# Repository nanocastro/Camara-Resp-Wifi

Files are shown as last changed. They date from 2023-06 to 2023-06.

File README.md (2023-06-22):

# Cámara de respiración de suelo

Prototipo portátil y de bajo costo para medir el flujo de CO2, la temperatura y la humedad del suelo y estimar su actividad microbiana.  

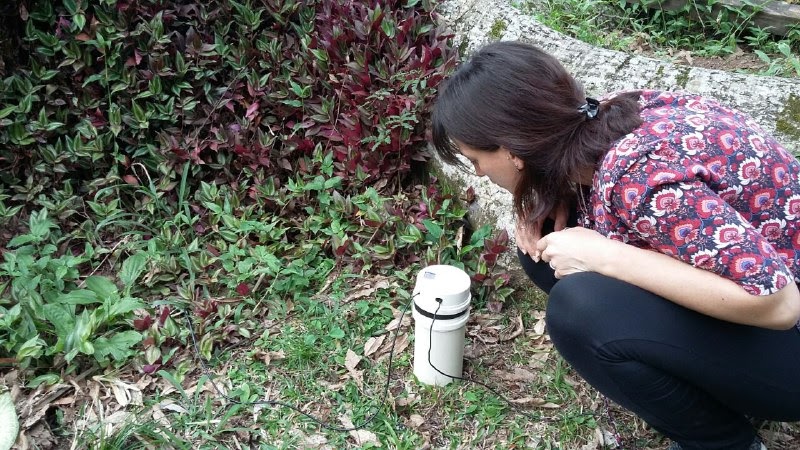
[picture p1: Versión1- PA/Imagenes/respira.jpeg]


Este prototipo es parte del trabajo que estamos desarrollando en el [Laboratorio agroecológico abierto](https://regosh.libres.cc/proyectos/lab-agroeco-abierto/) y el nodo [ReGOSH de Mendoza](https://regosh.libres.cc/).

Su desarrollo está basado en el [prototipo abierto de Hackteria](https://www.hackteria.org/wiki/CO2_Soil_Respiration_Chamber).  

El costo de este prototipo es de 2 órdenes de magnitud menor que el de una [cámara comercial](https://gitlab.com/nanocastro/camara-respiracion-suelo/-/blob/master/Presupuestos%20Nro%2012426.PDF).  

## Prototipos
Estos prototipos están aún en fase de desarrollo. Necesitamos testear en campo y mejorar la documentación y el diseño.

### Prototipo actual - Versión Mendoza

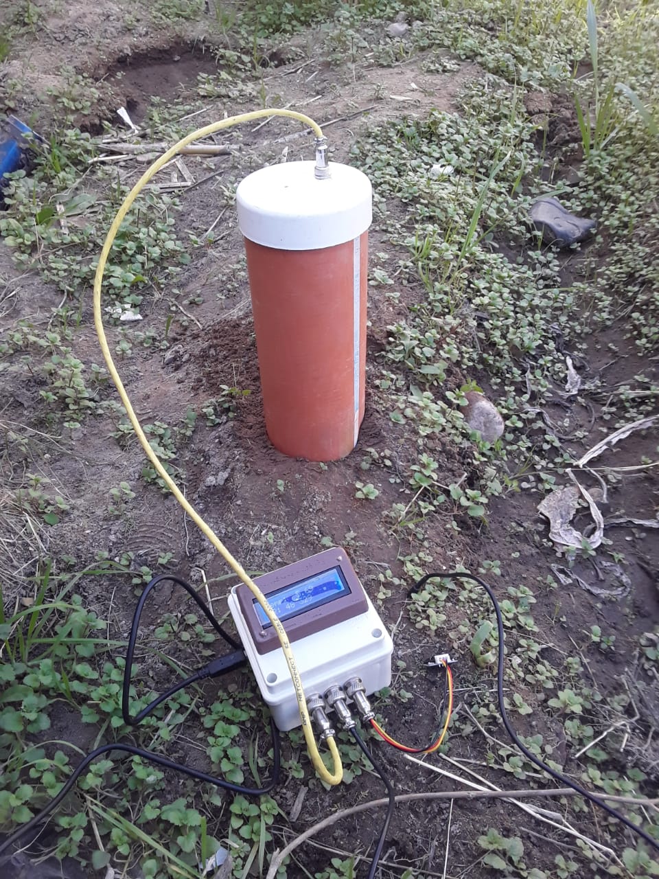
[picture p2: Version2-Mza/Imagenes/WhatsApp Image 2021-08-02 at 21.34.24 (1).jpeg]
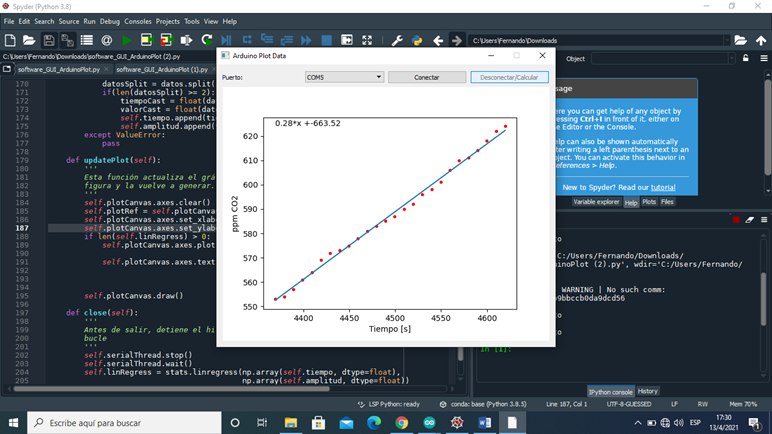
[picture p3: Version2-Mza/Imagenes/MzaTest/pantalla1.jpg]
 

Este prototipo utiliza el sensor de CO2 infrarrojo MH-Z19B que se coloca en el interior de una cámara para medir el flujo de CO2 y es controlado por una placa Arduino UNO. Los datos son transmitidos por bluetooth a un script de python que recibe los datos, los grafica en tiempo real y calcula la regresión lineal de un intervalo deseado. El dispositivo mide también la temperatura y la humedad de suelo

> [Aquí la documentación completa](/Version2-Mza) 

### Primer prototipo - Residencia Porto Alegre

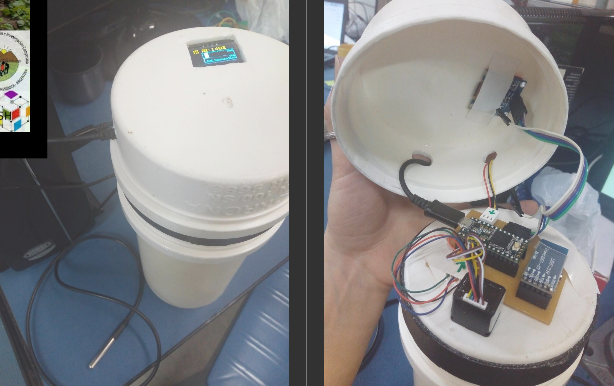
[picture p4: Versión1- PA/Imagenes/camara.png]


[Primer prototipo](/Versión1-%20PA) desarrollado en el marco de la residencia ReGOSH (Porto Alegre) financiadas por CYTED.   
Este dispositivo utiliza un sensor MH-Z16 y una placa Teensy 4.0. Los datos se visualizan en una pantalla OLED

### Cómo funciona y para que sirve una cámara de respiración de suelo?
[Aqui](/Referencias) puedes encontrar algunos documentos que explican el funcionamiento de las cámaras de respiración de suelo y presentan algunos de sus usos

### Licencia 
Este proyecto es de código abierto y se libera bajo [licencia CERN para hardware abierto](https://gitlab.com/nanocastro/camara-respiracion-suelo/-/blob/master/License). 

### Te interesa colaborar?

Si te interesa el proyecto y quisieras colaborar podes escribirnos a 

ferhcastro at gmail.com o pcremades at gmail.com

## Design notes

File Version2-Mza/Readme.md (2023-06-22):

# Cámara de Respiración de Suelo: Guía de armado
__Nodo reGOSH Mendoza - Equipo de Física Experimental II, FCEN - 2022__
## Descripción del dispositivo
El dispositivo puede medir la concentración de CO2, la temperatura y la humedad del suelo.  

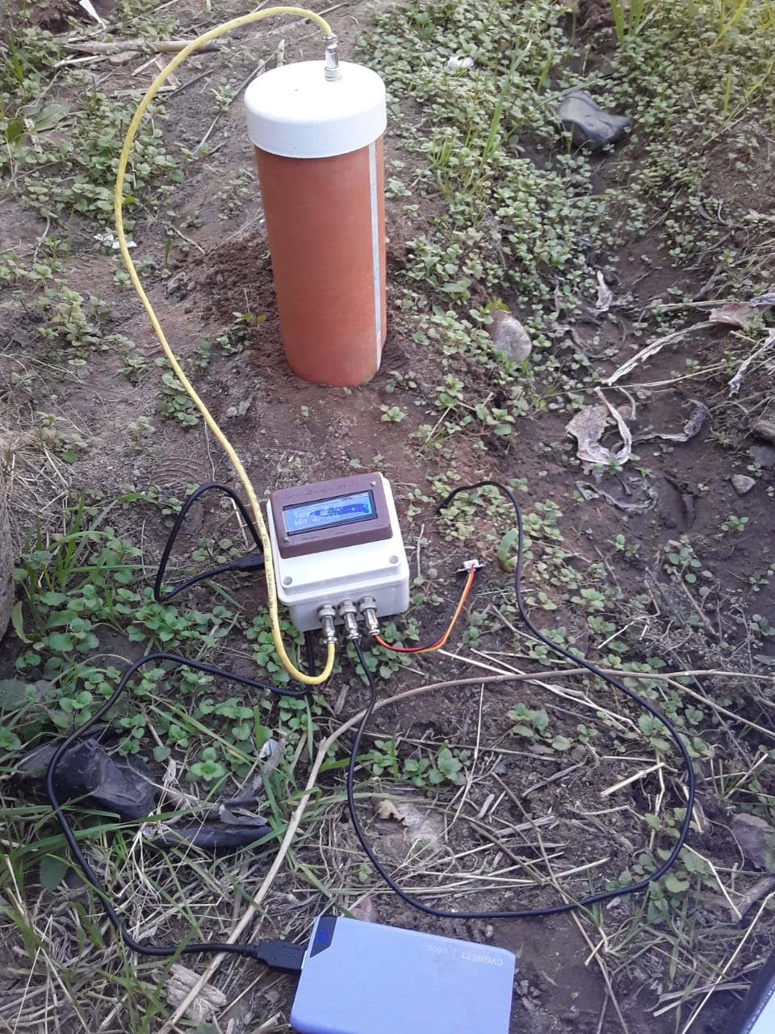
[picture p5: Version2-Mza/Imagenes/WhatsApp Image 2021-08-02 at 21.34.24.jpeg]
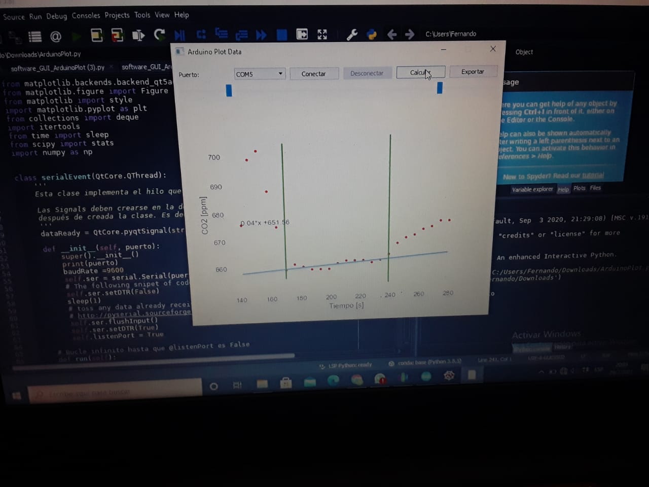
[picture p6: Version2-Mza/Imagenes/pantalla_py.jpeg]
 

## BOM
[Lista de materiales](/Version2-Mza/ListaMateriales.ods)

## Ensamblado
El dispositivo cuenta con 2 partes, una cámara donde se aloja el sensor de CO2 y una unidad de control que se encarga de la comunicación con los sensores y de enviar lsos datos vía bluetooth a una PC donde se pueden visualizar y analizar. 
__Herramientas necesarias:__

* Soldador de estaño
* Pistola de silicona
* 4 tornillos de 2 cm
* Alicate
* Taladro
* Mecha para taladro de 18mm

## (2) Cableado y test inicial
En primer lugar debemos probar que la electrónica funcione correctamente, para ello:

* Realizamos el cableado según la figura:

Atención! El módulo bluetooth lo debemos conectar luego de que esté cargado el firmware.
  
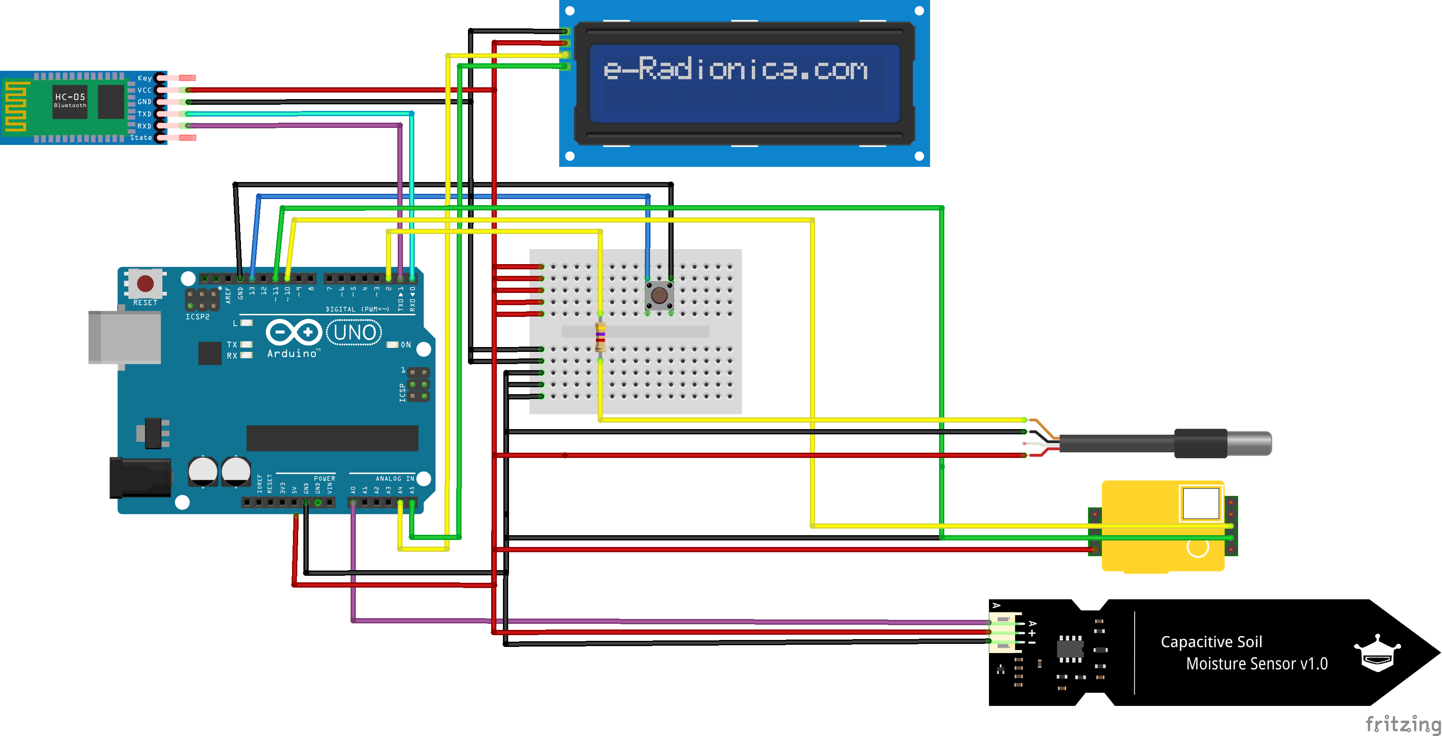
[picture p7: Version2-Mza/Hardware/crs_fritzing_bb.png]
Esquematico Fritzing
   

### Ensamblado cámara de respiración
La cámara está compuesta por un tramo de 15-20cm de caño sanitario de 110mm y una tapa para dicho caño.   
  
Una vez que hemos comprobado el correcto funcionamiento del dispositivo podemos colocar y cablear el sensor de CO2 dentro de la cámara de respiración.  

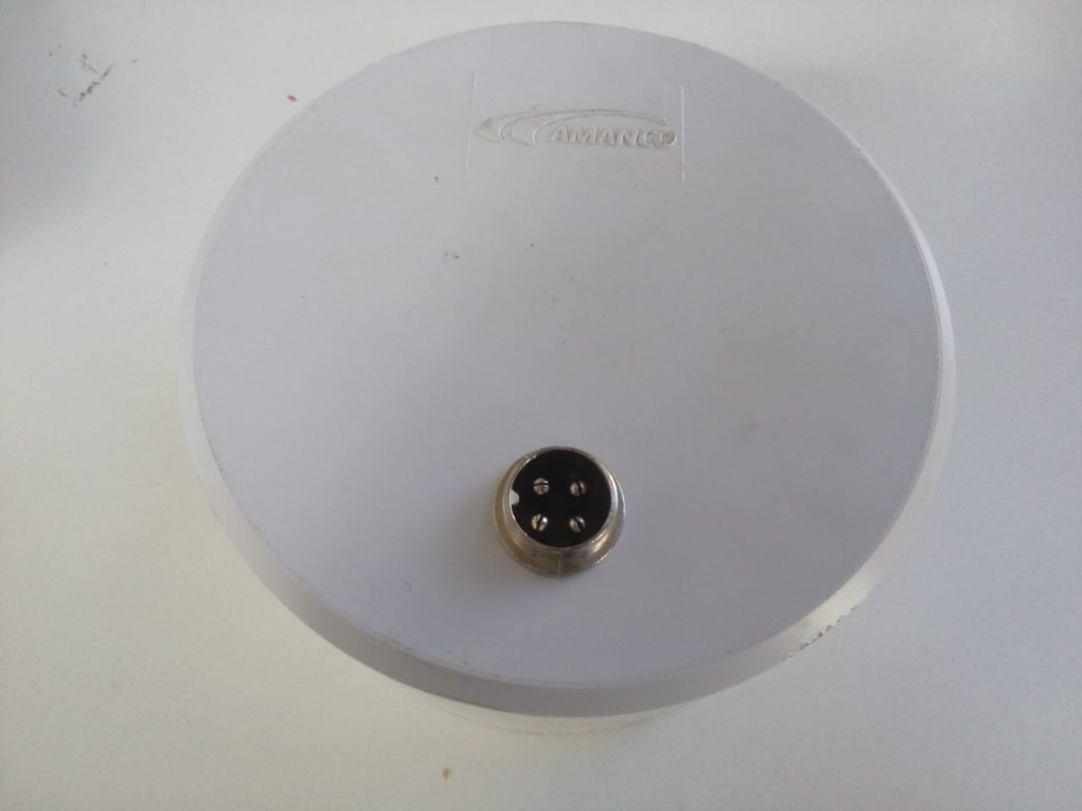
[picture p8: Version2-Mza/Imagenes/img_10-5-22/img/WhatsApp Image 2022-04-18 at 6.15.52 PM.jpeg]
   

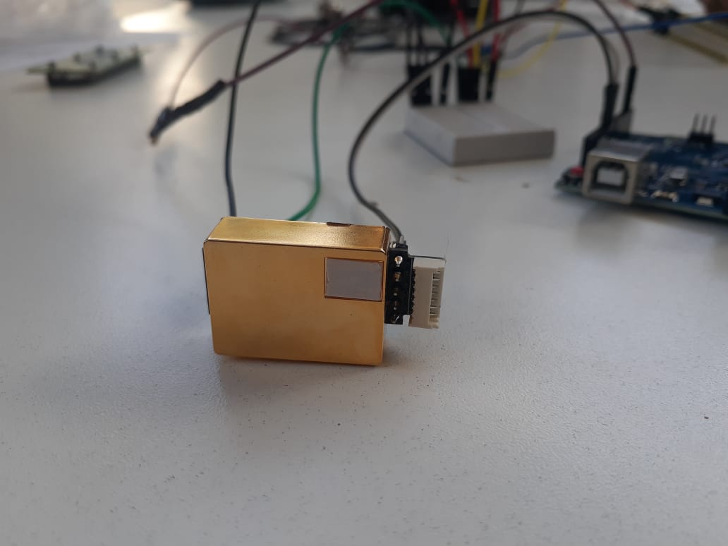
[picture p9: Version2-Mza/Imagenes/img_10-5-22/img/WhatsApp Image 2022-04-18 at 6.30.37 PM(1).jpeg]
     
Pegamos con silicona el [adaptador impreso](/Version2-Mza/Hardware/STL/mz_holder_soil_resp.stl) del sensor en el lado interno de la tapa y perforamos un hoyo del diámetro de la rosca del lado hembra de un conector GX12 de 4 pines.  
Luego pegamos el sensor al adaptador y colocamos el conector en la tapa.   

:eyes: Es conveniente soldar pines en el sensor de CO2 para facilitar su conexión.

:eyes: El módulo de bluetooth lo debemos conectar una vez que esté cargado el firmware.

## (3) Ensamblado de la cámara de respiración

La cámara está compuesta por un tramo de 15 a 20 cm de caño sanitario de 110 mm y una tapa para caño. (Ver Figura)

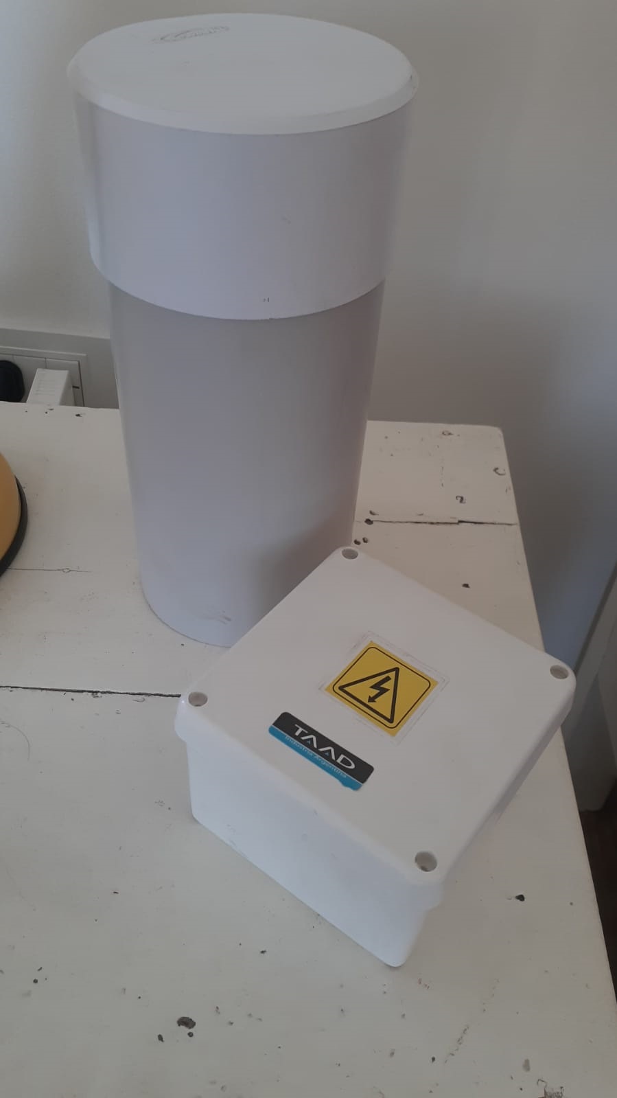
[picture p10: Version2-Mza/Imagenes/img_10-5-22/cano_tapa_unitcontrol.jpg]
  

Una vez que hemos comprobado el correcto funcionamiento del dispositivo (ver sección 2) podemos colocar y cablear el sensor de CO2 dentro de la cámara de respiración:

* Perforar con taladro un agujero del diámetro de la rosca del lado hembra de un conector GX12 de 4 pines.
* Colocar el conector en el agujero y fijar con silicona de ser necesario.
* Pegar con silicona el sensor de CO2 al adaptador.
* Atornillar la placa impresa, previamente unida al sensor, en la tapa de la cámara.

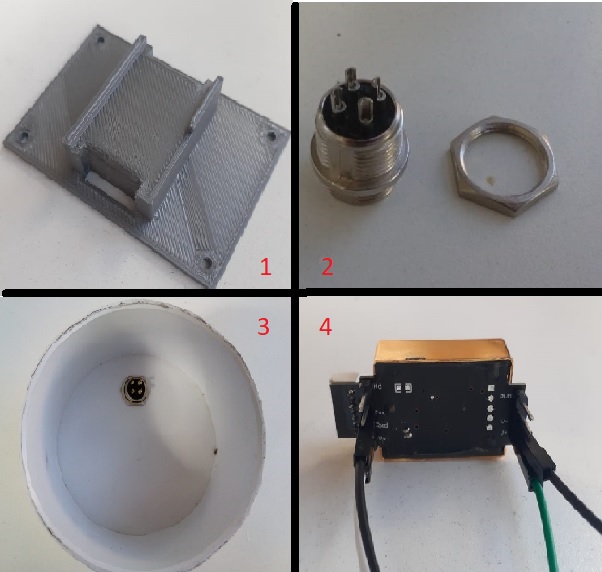
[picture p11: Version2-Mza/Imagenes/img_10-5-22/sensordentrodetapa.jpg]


1. Adaptador impreso para sensor CO2
2. Conector GX12 de 4 pines
3. Conector GX12 ya colocado en la tapa de la cámara previamente agujereada.
4. Sensor CO2 que se fijará en el adaptador impreso.

Aquí se muestra el resultado final de la instalación del sensor de CO2 en el lado interno de la tapa de la cámara de respiración de suelo:

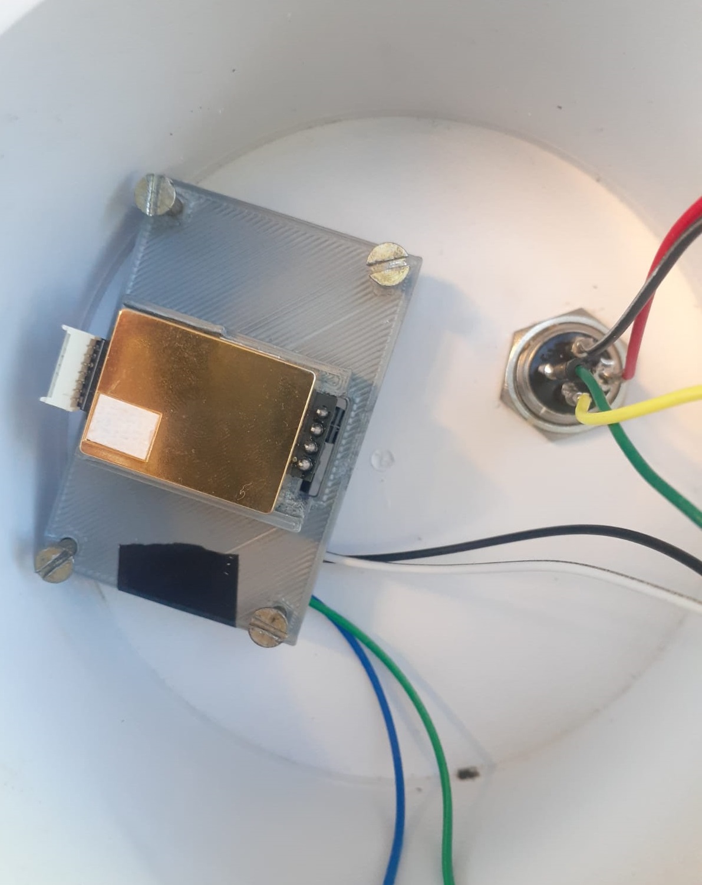
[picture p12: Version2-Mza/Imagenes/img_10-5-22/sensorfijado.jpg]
  

## (4) Ensamblado unidad de control 

La unidad de control está compuesta por una caja de peso plástica, una base para apoyar el Arduino y una carcasa para colocar el display.

* Fijar con silicona el soporte para placa Arduino en el fondo de la caja plástica.
* Usar el taladro con mecha 18 mm para hacer 3 agujeros en el frente de la caja de paso. Los agujeros tendrán que tener un diámetro acorde a los conectores GX12 de 3 pines.
* En nuestro caso, fue necesario agregar una cuarta perforación en el lado trasero de la caja. Esto se hizo para poder conectar nuestra placa Arduino UNO con su transformador 9V.

Aquí mostramos la unidad de control con las perforaciones realizadas:

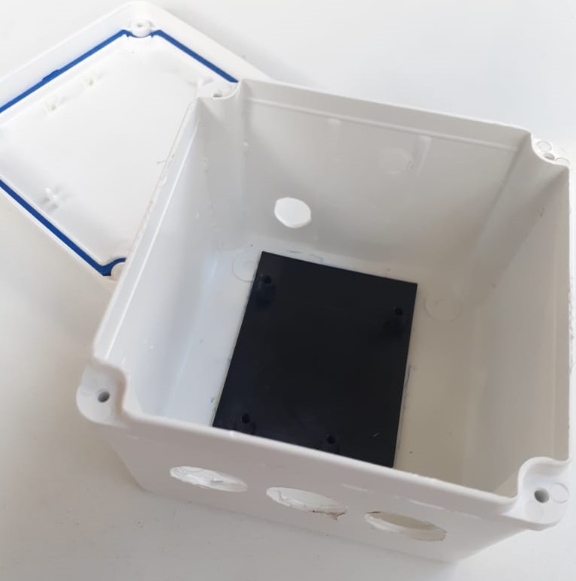
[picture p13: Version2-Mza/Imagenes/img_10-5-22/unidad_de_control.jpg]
  

## (5) Conexiones

En esta etapa realizaremos las conexiones necesarias para el funcionamiento de los sensores. También es necesario replicar conexiones especificadas en la sección (2), pero esta vez en la unidad de control. Será necesario utilizar estaño y soldadora.

### Conexión: unidad de control - cámara de respiración
Se necesita armar un cable para conectar la unidad de control con la cámara de respiración. Para ello utilizamos un cable de 4 hilos y los lados macho de 2 conectores GX12 de 4 pines.
### Conexión: Conectores GX12 ficha hembra - Placa Arduino
Para los sensores de humedad y temperatura se utilizan 2 conectores GX12 de 3 pines:
* El lado hembra se conecta en un agujero perforado en la caja plástica y se conectan los cables de conexión al Arduino.
* Al lado macho se conectan los cables provenienties de los sensores.
* Fijar las fichas de los conectores en los agujeros de la caja de paso.

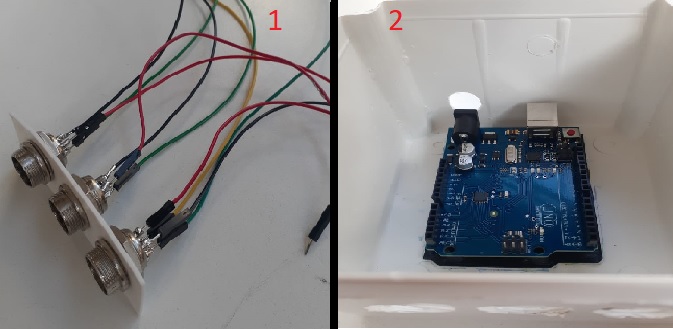
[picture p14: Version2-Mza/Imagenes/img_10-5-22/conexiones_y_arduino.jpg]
  
1. Unión del lado hembra de conectores GX12 con el cableado de cada sensor hacia la placa Arduino.
2. Placa Arduino, ya fijada en la unidad de control.

### Conexión: Sensores - Conector GX12 ficha macho
* Para el sensor de temperatura simplemente soldar su cable de 3 hilos con el lado macho del conector.
* Para entender la conexión del sensor de humedad ver Figura debajo. Se debe conectar el lado A de la placa de la ficha con la ficha macho del conector GX12. El cableado B corresponde a la cabecera del sensor de humedad.

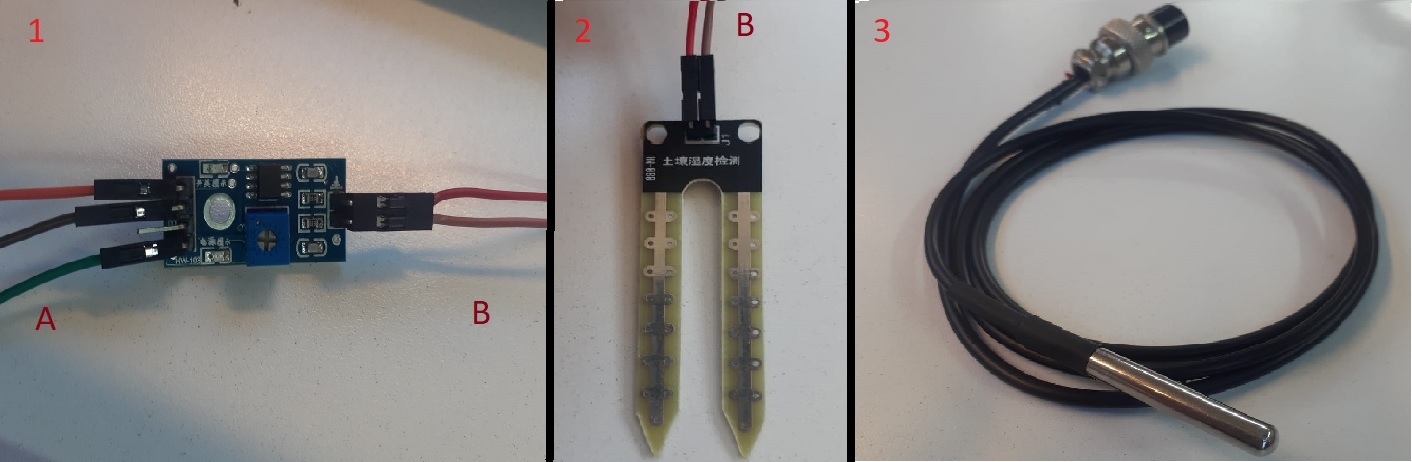
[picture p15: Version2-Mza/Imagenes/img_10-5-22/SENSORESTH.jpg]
  
1. Placa de circuitos del sensor de humedad.
2. Cabecera del sensor de humedad.
3. Conexión del sensor de temperatura a ficha macho del conector GX12

### Conexión: Módulo BT - Placa Arduino

Esta conexión debe realizarse luego de corroborar el correcto funcionamiento de los sensores y el firmware.
* Utilizar cables conectores con ficha macho-hembra para la conexión del módulo BT con la placa Arduino.

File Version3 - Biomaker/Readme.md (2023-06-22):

 ### Biomaker Hackster Project presentation
 
[Biomaker 2022](https://www.hackster.io/432701/low-cost-soil-respiration-system-to-assess-soil-health-3263b7)

### CO2 sensirion sensor 
[SCD41](https://www.sensirion.com/en/environmental-sensors/evaluation-kit-sek-environmental-sensing/evaluation-kit-sek-scd41/) 
Includes Arduino code  
[Seed docs](https://www.seeedstudio.com/Grove-CO2-Temperature-Humidity-Sensor-SCD41-p-5025.html)

### MH-Z16
[Arduino Library](https://github.com/SandboxElectronics/NDIRZ16)  
[Datasheet](https://www.winsen-sensor.com/d/files/MH-Z16.pdf)  

### Arduino
[Starter kit](https://wiki.seeedstudio.com/Grove-Beginner-Kit-For-Arduino/)

### References
Some interesting references 
- [SMAAC](https://gitlab.com/nanocastro/camara-respiracion-suelo/-/blob/master/Referencias/Talking_SMAAC_A_New_Tool_to_Measure_Soil_Respirati.pdf)
- [ResTox](https://gitlab.com/nanocastro/camara-respiracion-suelo/-/blob/master/Referencias/djerdj2021.pdf)  
[Soft Github repo](https://github.com/gyorgytamara/restox-software)  
[Sup Material](https://gitlab.com/nanocastro/camara-respiracion-suelo/-/tree/master/Versionn%203%20-%20Biomaker/SupMaterial)  
- [Metabolt](https://gitlab.com/nanocastro/camara-respiracion-suelo/-/blob/master/Referencias/sensors-20-04479.pdf)

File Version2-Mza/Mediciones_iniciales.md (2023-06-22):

### Mediciones en aire ambiente
En las mediciones en aire ambiente se observa que el sensor responde a eventos tales como apertura de puertas, aumento de concentración en espacio cerrado con gente.
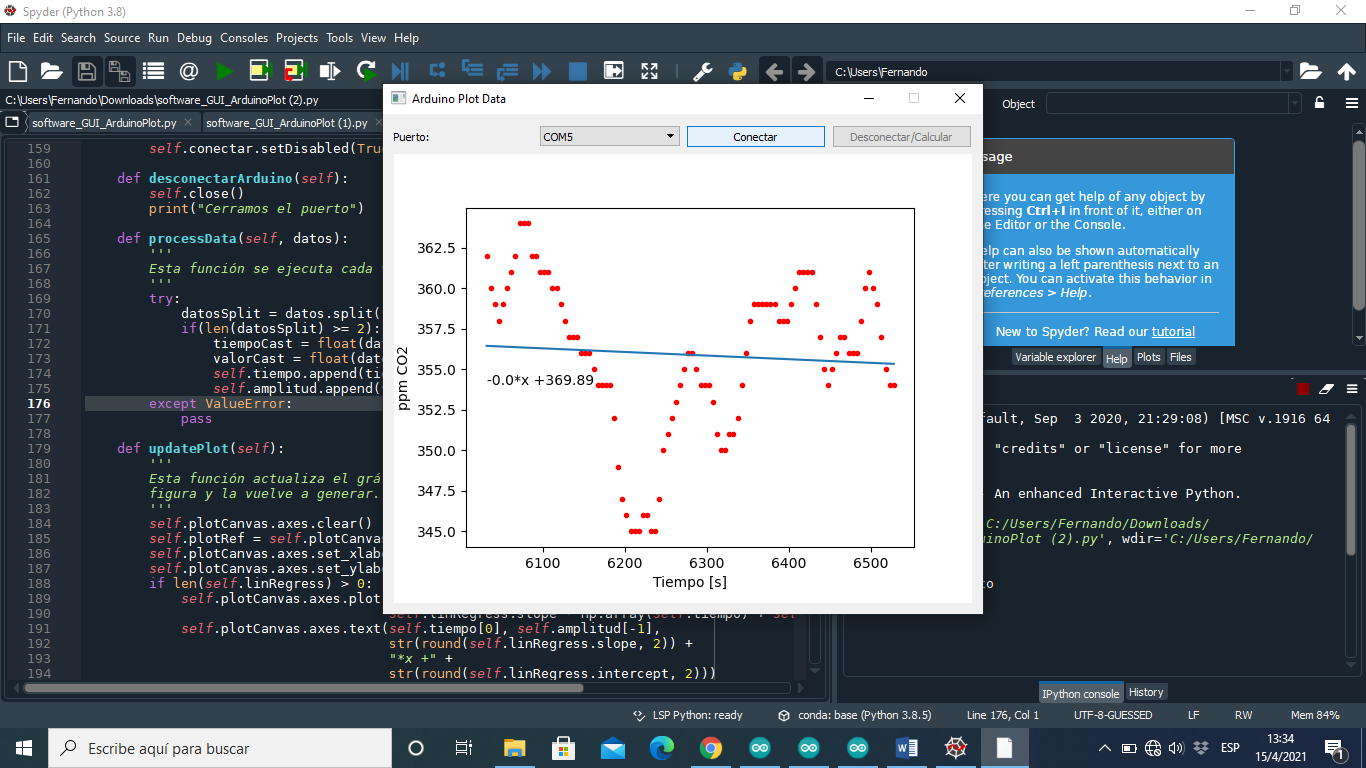
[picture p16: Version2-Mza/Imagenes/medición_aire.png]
Aire ambiente
  
En este momento aún no se podía exportar el gráfico por lo que se muestra una captura de pantalla. La regresión tiene pendiente 0.0 integrando en aprox 5 minutos y una rango de variación de aprox 40ppm. 

### Mediciones en la cámara cerrada
Analizamos la estabilidad de la medición dejando la cámara abierta al aire durante unos minutos y luego colocamos una tapa para que quedara cerrada. 
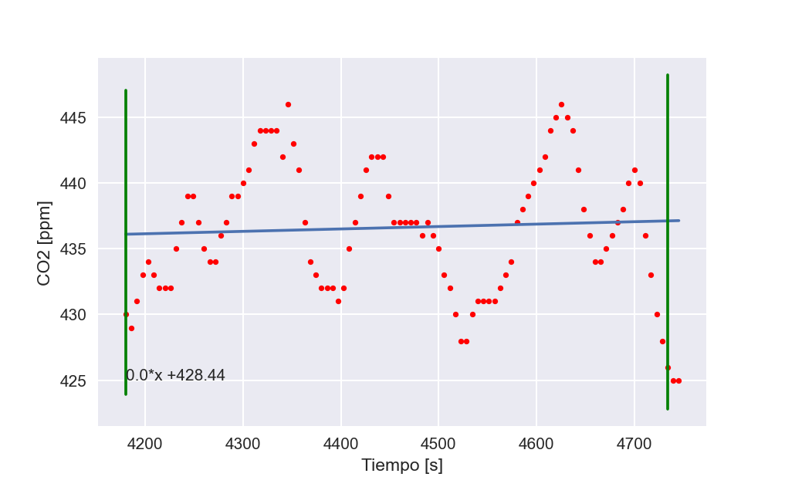
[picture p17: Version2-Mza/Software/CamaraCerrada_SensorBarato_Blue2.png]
Cámara cerrada
  
Si bien se observa un variabilidad es menor que en aire ambiente aprox 20ppm.  

### Mediciones en suelo
Realizamos mediciones en el suelo en periódos breves de 2 minutos aprox.   
* Huerta urbana  
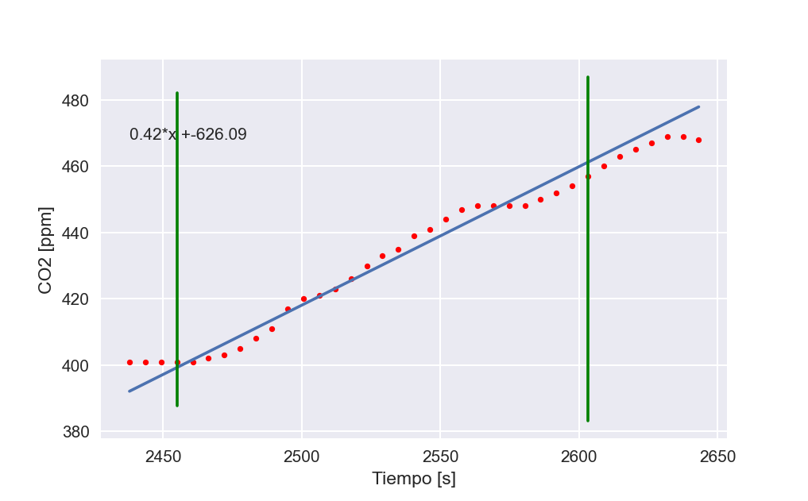
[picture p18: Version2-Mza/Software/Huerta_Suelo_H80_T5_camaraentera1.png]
  
A partir de la pendiente (tasa de variación de la concentración) se puede calcular el flujo de CO2
Entre medición y medición se observó bastante variabilidad en la pendiente.   
* Tierra preparada
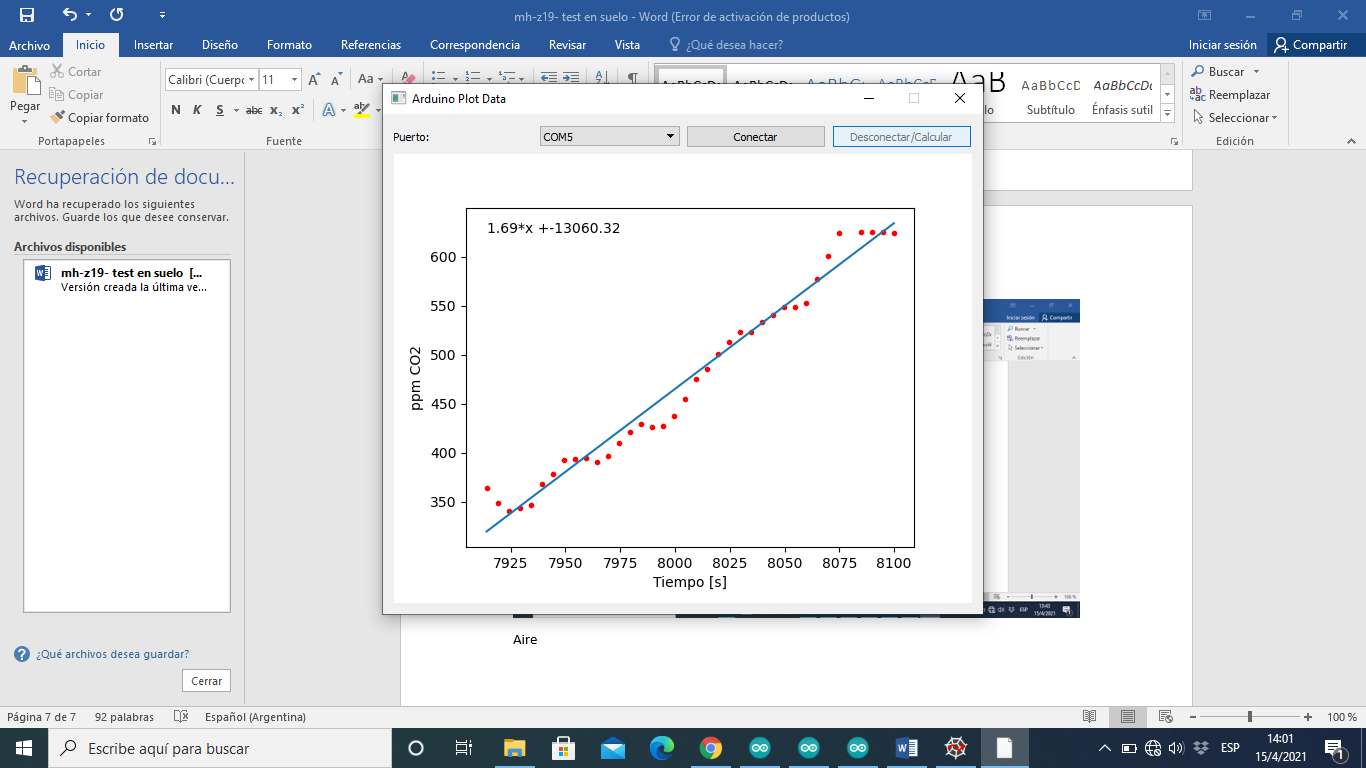
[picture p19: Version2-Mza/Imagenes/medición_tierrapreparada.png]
Tierra preparada

Es necesario establecer un protocolo de medición. Se puede tomar como referencia el protocolo de LICOR
También es necesario asegurar que la cámara quede sellada contra el suelo o colocar un collar de medición.

### Medición de temperatura y humedad
La medición de temperatura y humedad del suelo es bastante estable. Las mediciones se presentan en la pantalla de la unidad de control 
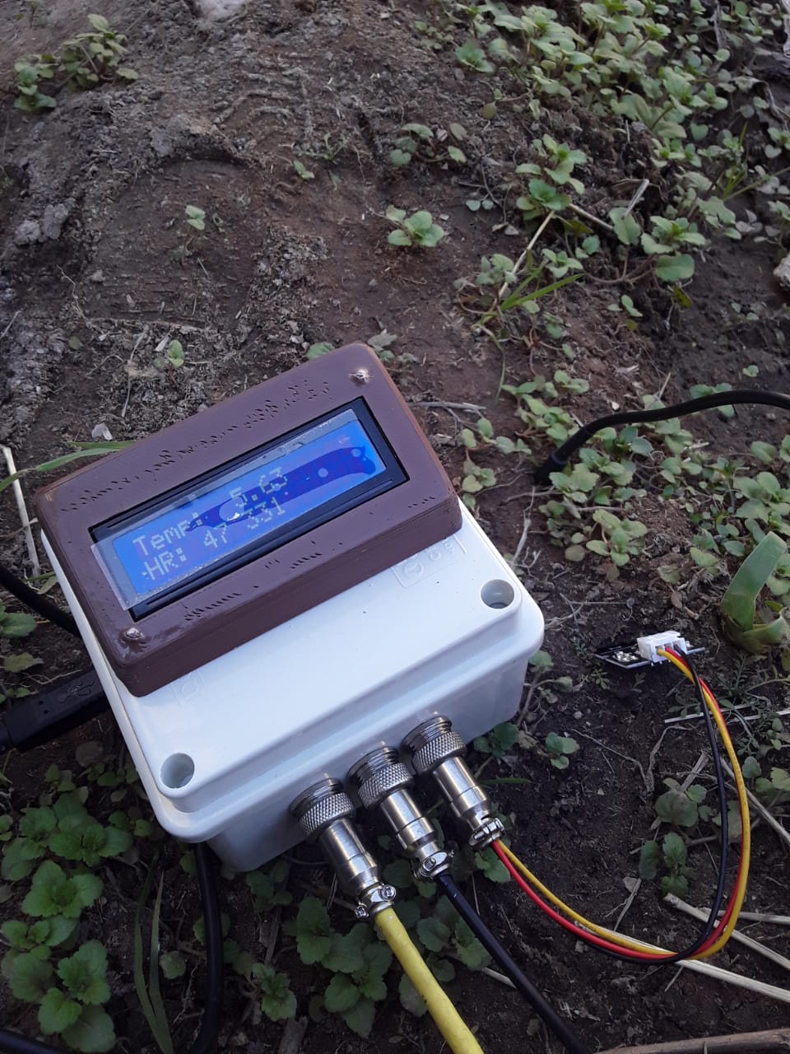
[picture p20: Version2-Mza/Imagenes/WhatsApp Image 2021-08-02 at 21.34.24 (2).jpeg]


Algunas cuestiones referidas a el sensor capacitivo de humedad

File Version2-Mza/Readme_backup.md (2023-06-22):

# Descripción del dispositivo
El dispositivo puede medir la concentración de CO2, la temperatura y la humedad del suelo.  

SRC SRC

## BOM
[Lista de materiales](/Version2-Mza/ListaMateriales.ods)

## Ensamblado
El dispositivos cuenta con 2 partes, una cámara donde se aloja el sensor de CO2 y una unidad de control que se encarga de la comunicación con los sensores y de enviar los datos via bluetooth a una PC donde se pueden visualizar y analizar.  
**Herramientas necesarias:**
* Soldador de estaño
* Pistola de siliconas
* Alicate

### Cableado y test inicial
En primer lugar debemos probar que la electrónica funcione correctamente. Para ello realizamos el cableado según el esquemático y luego cargamos firmware para chequear el funcionamiento.
Es conveniente soldar pines en el sensor de CO2 para facilitar su conexión.   

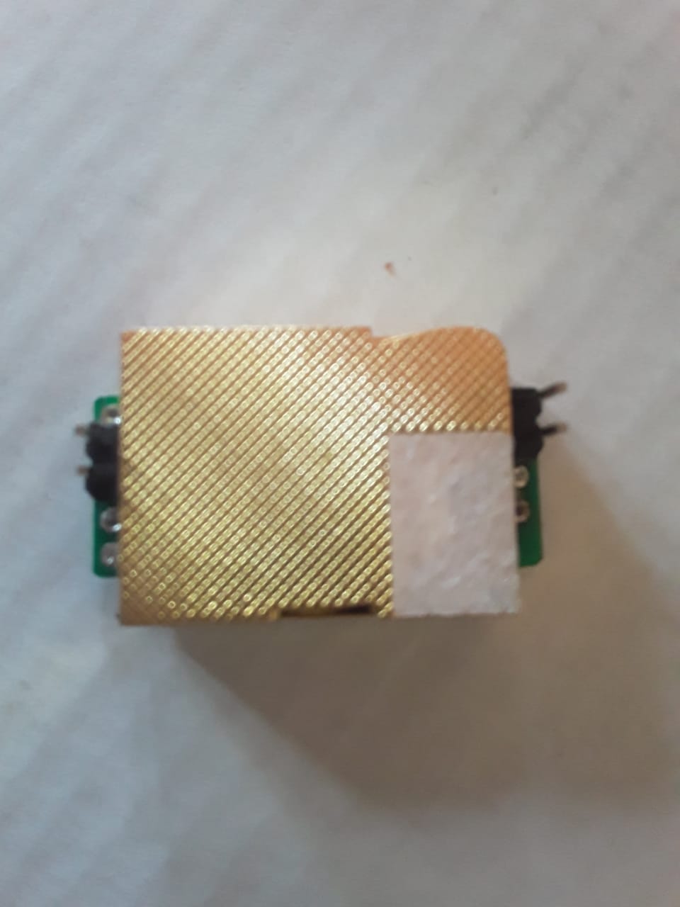
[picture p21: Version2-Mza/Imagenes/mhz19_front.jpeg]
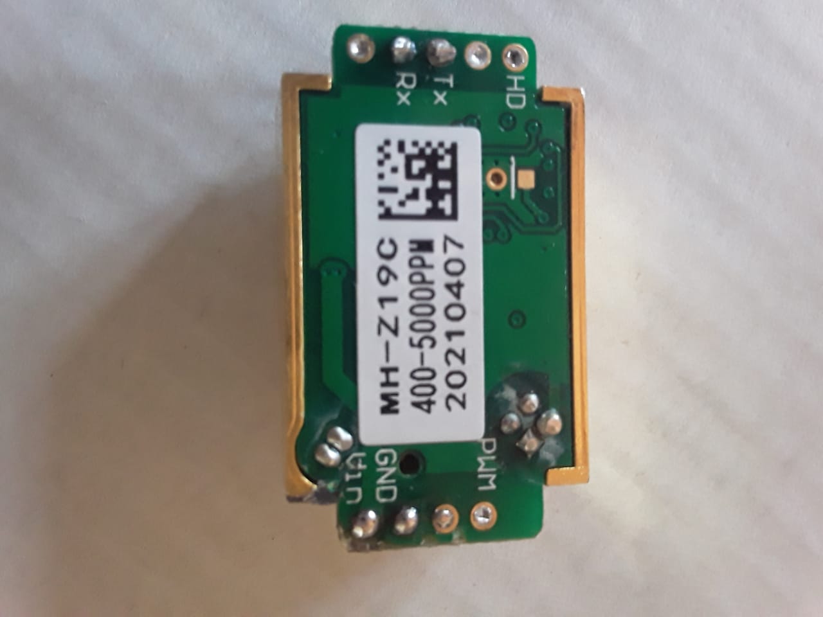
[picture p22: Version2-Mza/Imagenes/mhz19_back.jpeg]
    

Atención! El módulo bluetooth lo debemos conectar luego de que esté cargado el firmware.  
Esquematico Fritzing   

### Ensamblado cámara de respiración
La cámara está compuesta por un tramo de 15-20cm de caño sanitario de 110mm y una tapa para dicho caño.   

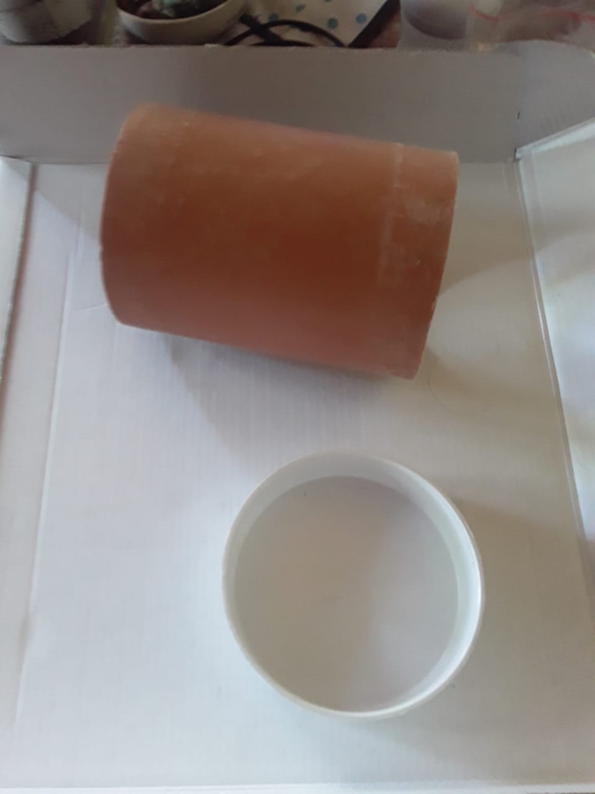
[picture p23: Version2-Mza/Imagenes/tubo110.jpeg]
caño sanitario 110
   
  
Una vez que hemos comprobado el correcto funcionamiento del dispositivo podemos colocar y cablear el sensor de CO2 dentro de la cámara de respiración.  
Pegamos con silicona el [adaptador impreso](/Version2-Mza/Hardware/STL/mz_holder_soil_resp.stl) del sensor en el lado interno de la tapa y perforamos un hoyo del diámetro de la rosca del lado hembra de un conector GX12 de 4 pines.  
Luego pegamos el sensor al adaptador y colocamos el conector en la tapa.   

### Cable de conexión 
Se necesita armar un cable para conectar la unidad de control con la cámara de respiración. Para ello utilizamos un cable de 4 hilos y los lados macho de 2 conectores GX12 de 4 pines.

### Ensamblado unidad de control  
La unidad de control está compuesta por una caja de paso plástica, una base para apoyar el Arduino y una carcaza para colocar el display.  
Para los sensores de humedad y temperatura se utilizan 2 conectores GX12 de 3 pines.  El lado hembra se conecta en un agujero perforado en la caja plástica y se conectan los cables de conexión al Arduino. Al lado macho se conectan a los cables de los sensores.  
Una vez colocada la base para el Arduino en el fondo de la caja se mide y se corta la misma para permitir la entrada de la alimentación/USB.  
 
## Firmware
Última versión del [firmware](Version2-Mza/Firmware/CO2_serial_py_LCD_Temp/CO2_serial_py_LCD_Temp.ino)
El firmware se carga por medio de la [IDE de Arduino](https://www.arduino.cc/en/software)  

Librerias  utilizadas
* Para el MH-Z19 se utiliza una [librería](https://github.com/WifWaf/MH-Z19) que permite medir por debajo de 400ppm 
	
* Las libreías de la pantalla (LiquidCristal_I2C) y del sensor de temperatura (DSB18B20) se pueden descargar directamente del gestor de librerías de la IDE.  

## Software
[Aplicación de Python](https://gitlab.fcen.uncu.edu.ar/pcremades/co2-chamber-plot) para visualizar y analizar los datos en tiempo real desarrollada por Pablo Cremades.

[Soft alternativo](https://snapcraft.io/tauno-serial-plotter) para graficar el serial   

## Primeras experiencias
Realizamos una serie de [mediciones preliminares](/Version2-Mza/Mediciones_iniciales.md) para estudiar la respuesta de sensor. 

## Protocolos de medición
[Aquí](/Referencias/Talking_SMAAC_A_New_Tool_to_Measure_Soil_Respirati.pdf) se puede encontrar una referencia de las distintas formas de medir con algunas indicaciones de los protocolos  
- En campo -> mediciónes de 2 minutos
  - [protocolo de LICOR](https://www.youtube.com/watch?v=1EkkB8JaIzQ&ab_channel=MethodsinSoilOrganicMatterandBiogeochemistry)   
- En laboratorio - 24h burst test
  - [protocolo de Solvita](https://www.youtube.com/watch?v=_x7i7pDybJI)
- Soil induced respiration

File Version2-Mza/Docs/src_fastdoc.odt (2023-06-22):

Soil respiration chamber – MZA prototype

I still have to document but this is a fast and ugly overview of the setup

BOM

Electronics:

- MH-Z19 CO2 sensor

- DSB18B20 Temp sensor

- Soil humidity capacitive sensor

- Bluetooth HC-05

- Arduino UNO

- Arduino UNO protoboard

- calibration button

- 4.7k resistance

- LCD 16x2 I2C

Chamber:

- 110mm sanitary pipe

Hardware conections

Component | Pin | Arduino pin
MH-Z19 | Gnd | Gnd
MH-Z19 | Vcc | 5V
MH-Z19 | Rx | 11
MH-Z19 | Tx | 10
DSB18B20 | Gnd/Black | Gnd
DSB18B20 | Vcc/Red | 5V
DSB18B20 | Signal/Yellow | 2 (4.7k resistance)
Humidity sensor | Gnd | Gnd
Humidity sensor | Vcc | 3.3V
Humidity sensor | Signal | A0
Bluetooth | Vcc | 5V
Bluetooth | Gnd | Gnd
Bluetooth | Tx | 0
Bluetooth | Rx | 1
LCD I2C | Vcc | 5V
LCD I2C | Gnd | Gnd
LCD I2C | SDA
LCD I2C | SCL

Firmware

Libraries:

- new MH-z19 library (can go under 400ppm)

https://github.com/WifWaf/MH-Z19

- Liquid cristal I2C

- dsb18b20

The .ino code is in this folder

Software

We use a python script to read and graph live data coming from serial port.

When the measurement stops the script runs a linear regression of the selected data interval

Pablo Cremades (my electronic local partner also from GOSH) made the script and you can find it here:

https://tecnologias.libres.cc/pablocremades/camara-respiracion-suelo/blob/master/software/GUI/ArduinoPlot.py

If you think we can add some features just drop an issue


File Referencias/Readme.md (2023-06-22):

# Entendiendo la respiración de suelos

### Fundamentación_Concentración de CO2 como indicador de actividad microbiológica del suelo.

La descomposición de la materia orgánica es un proceso ecosistémico mediado por organismos heterótrofos que utilizan al material orgánico muerto o detritus como hábitat y fuente de carbono y energía, este gas se produce, fundamentalmente, a través del metabolismo de la microflora y de las 
raíces de la planta, siendo la descomposición microbiana de compuestos orgánicos el proceso más importante que lo genera. Durante la descomposición una parte del carbono es devuelto a la atmósfera en forma de CO2 , mientras que otra se transforma en otros compuestos más sencillos o se almacena 
en las propias estructuras microbianas (Pérez et al., 1998). En particular, la respiración metabólica de la comunidad de organismos asociados al detritus orgánico es el proceso que libera el carbono hacia la atmósfera en forma de CO2 . De esta manera,la respiración heterotrófica contribuye a la descomposición, junto a otros procesos como la humificación y la fragmentación del detritus (Carmona et al., 2006). 
Los microorganismos respiran continuamente y la tasa de respiración es un índice confiable de la tasa de crecimiento. Los factores que afectan el crecimiento también influyen en la respiración en el mismo grado.
La evolución del CO2 es un parámetro ligado al manejo de materiales orgánicos el cual representa una medición integral de la respiración del suelo, conocida como respiración edáfica basal (respiración de las raíces, fauna del suelo y la mineralización del carbono a partir de diferentes “pools” del carbono de suelo y desechos), es decir, representa la estimación de la actividad microbiana (García y Rivero, 2008). Frankenberger y Dick (1983, citado por Ajwa et al., 1999), señalaron que existe una relación muy estrecha entre la actividad biológica de un suelo y su fertilidad por lo que parámetros vinculados a la primera
han sido propuestos como indicadores apropiados del mencionado impacto, uno de ellos es la producción de CO2 (como reflejo del sustrato carbonado consumido por los microorganismos), el carbono o el nitrógeno unido a la biomasa microbiana y la actividad de las enzimas del suelo (Ajwa et al., 1999).

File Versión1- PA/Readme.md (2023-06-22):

### Primer prototipo - Residencia Porto Alegre



[Primer prototipo](/Versión1-%20PA) desarrollado en el marco de la residencia ReGOSH (Porto Alegre) financiadas por CYTED.   
Este dispositivo utiliza un sensor MH-Z16 y una placa Teensy 4.0. Los datos se visualizan en una pantalla OLED

# Camara respiración de suelo - Residencia Porto Alegre

### Diseço de placa_ 

Acá se puede ver la placa en pcb de la cámara de respiración, como algunos complementos que fueron creados para el mismo 
https://gitlab.com/nodo-mendoza/camara-respiracion-suelo/tree/master/hardware/electronics
También pueden ver algunos inconvenientes que se nos presentaron aquí https://gitlab.com/nodo-mendoza/camara-respiracion-suelo/issues/3

### Fresadora_

Los archivos digitales para la fresadora se hicieron tomando como guía el siguiente trabajo
http://cta.if.ufrgs.br/projects/estacao-meteorologica-modular/wiki/Placa_de_Controle,
donde se modificaron parámetros de acuerdo a las características específicas del proyecto como del tipo de fresadora utilizada.
Lo anterior descripto se puede observar aqui https://gitlab.com/nodo-mendoza/camara-respiracion-suelo/tree/master/hardware/electronics/placa_1/gCode/ngc
imágenes dd157eda80d9fbdee688e2e542551893808dbe02

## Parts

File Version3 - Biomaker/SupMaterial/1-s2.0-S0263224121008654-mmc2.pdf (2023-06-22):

## A low-cost versatile system for continuous real-time respiratory activity

## measurement as a tool in environmental research

### Tamara Djerdj¹

### , Vesna Peršić¹

### , Davorka K. Hackenberger¹

### , Domagoj K. Hackenberger¹

, Branimir K.

### Hackenberger¹,*

1
Josip Juraj Strossmayer University of Osijek, Department of Biology, Cara Hadrijana 8/A, HR-

### 31000 Osijek, Croatia

* To whom correspondence should be addressed at Josip Juraj Strossmayer University of Osijek,

### Department of Biology, Cara Hadrijana 8/A, 31000 Osijek, Croatia

### Fax: +385 31 399-939. Phone: +385 31 399-910. E-mail: hackenberger@biologija.unios.hr

# Supplementary Material S2. Drawings and assembly of 3D printed parts

### Models designed in FreeCAD

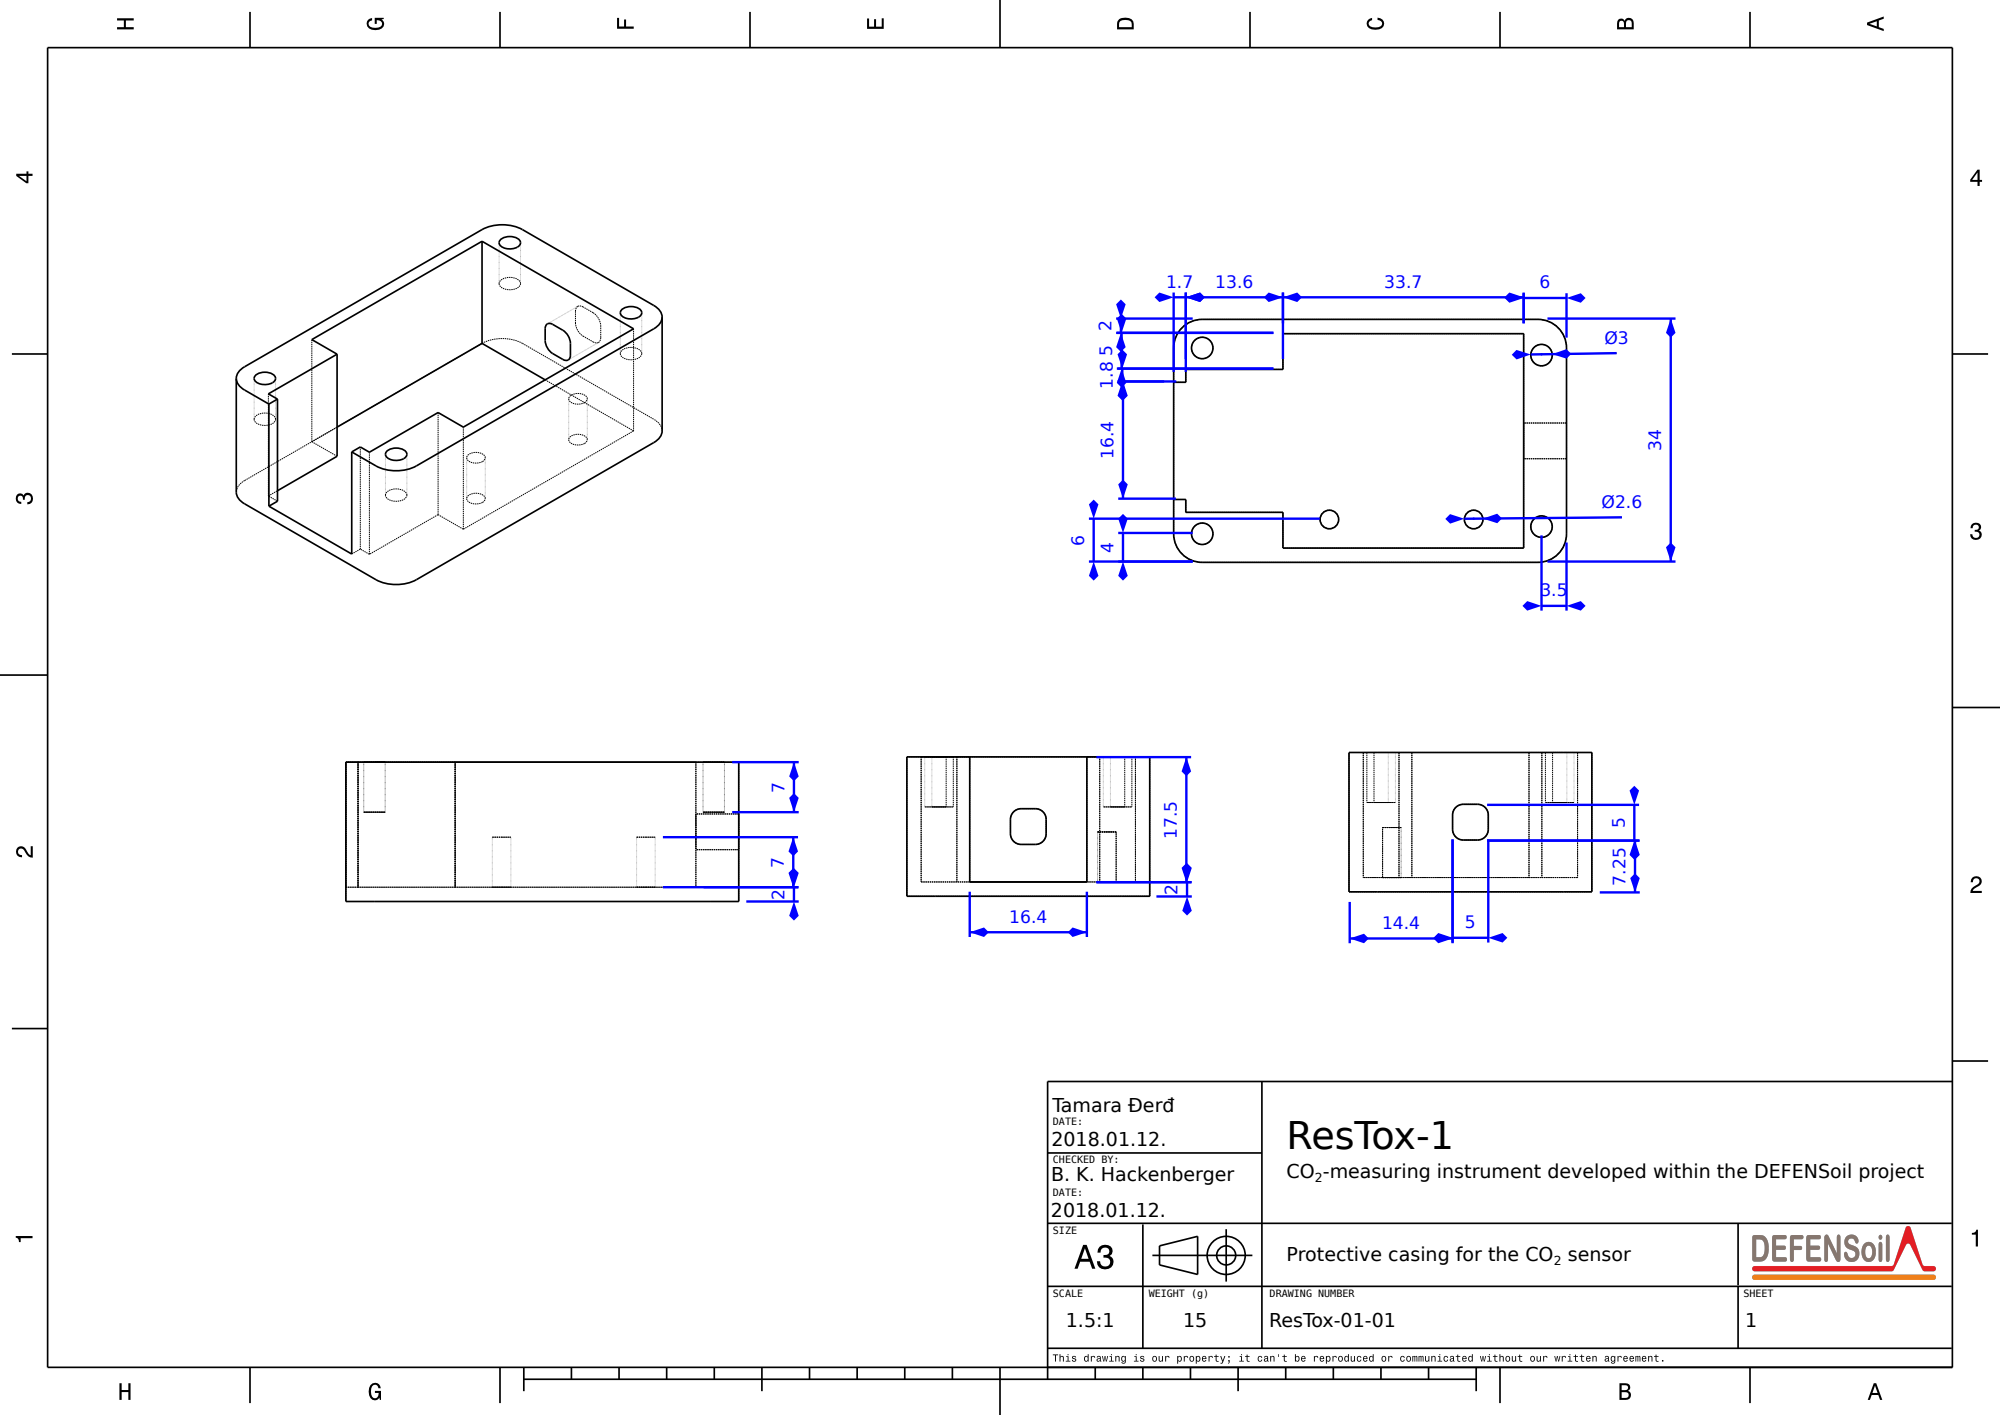
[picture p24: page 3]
Tamara Đerđ; B. K. Hackenberger; ResTox-1; DATE:; CHECKED BY:

CO2-measuring instrument developed within the DEFENSoil project

SIZE | | Protective casing for the CO2 sensor

SCALE 1.5:1 | WEIGHT (g) 15 | DRAWING NUMBER ResTox-01-01 | SHEET 1

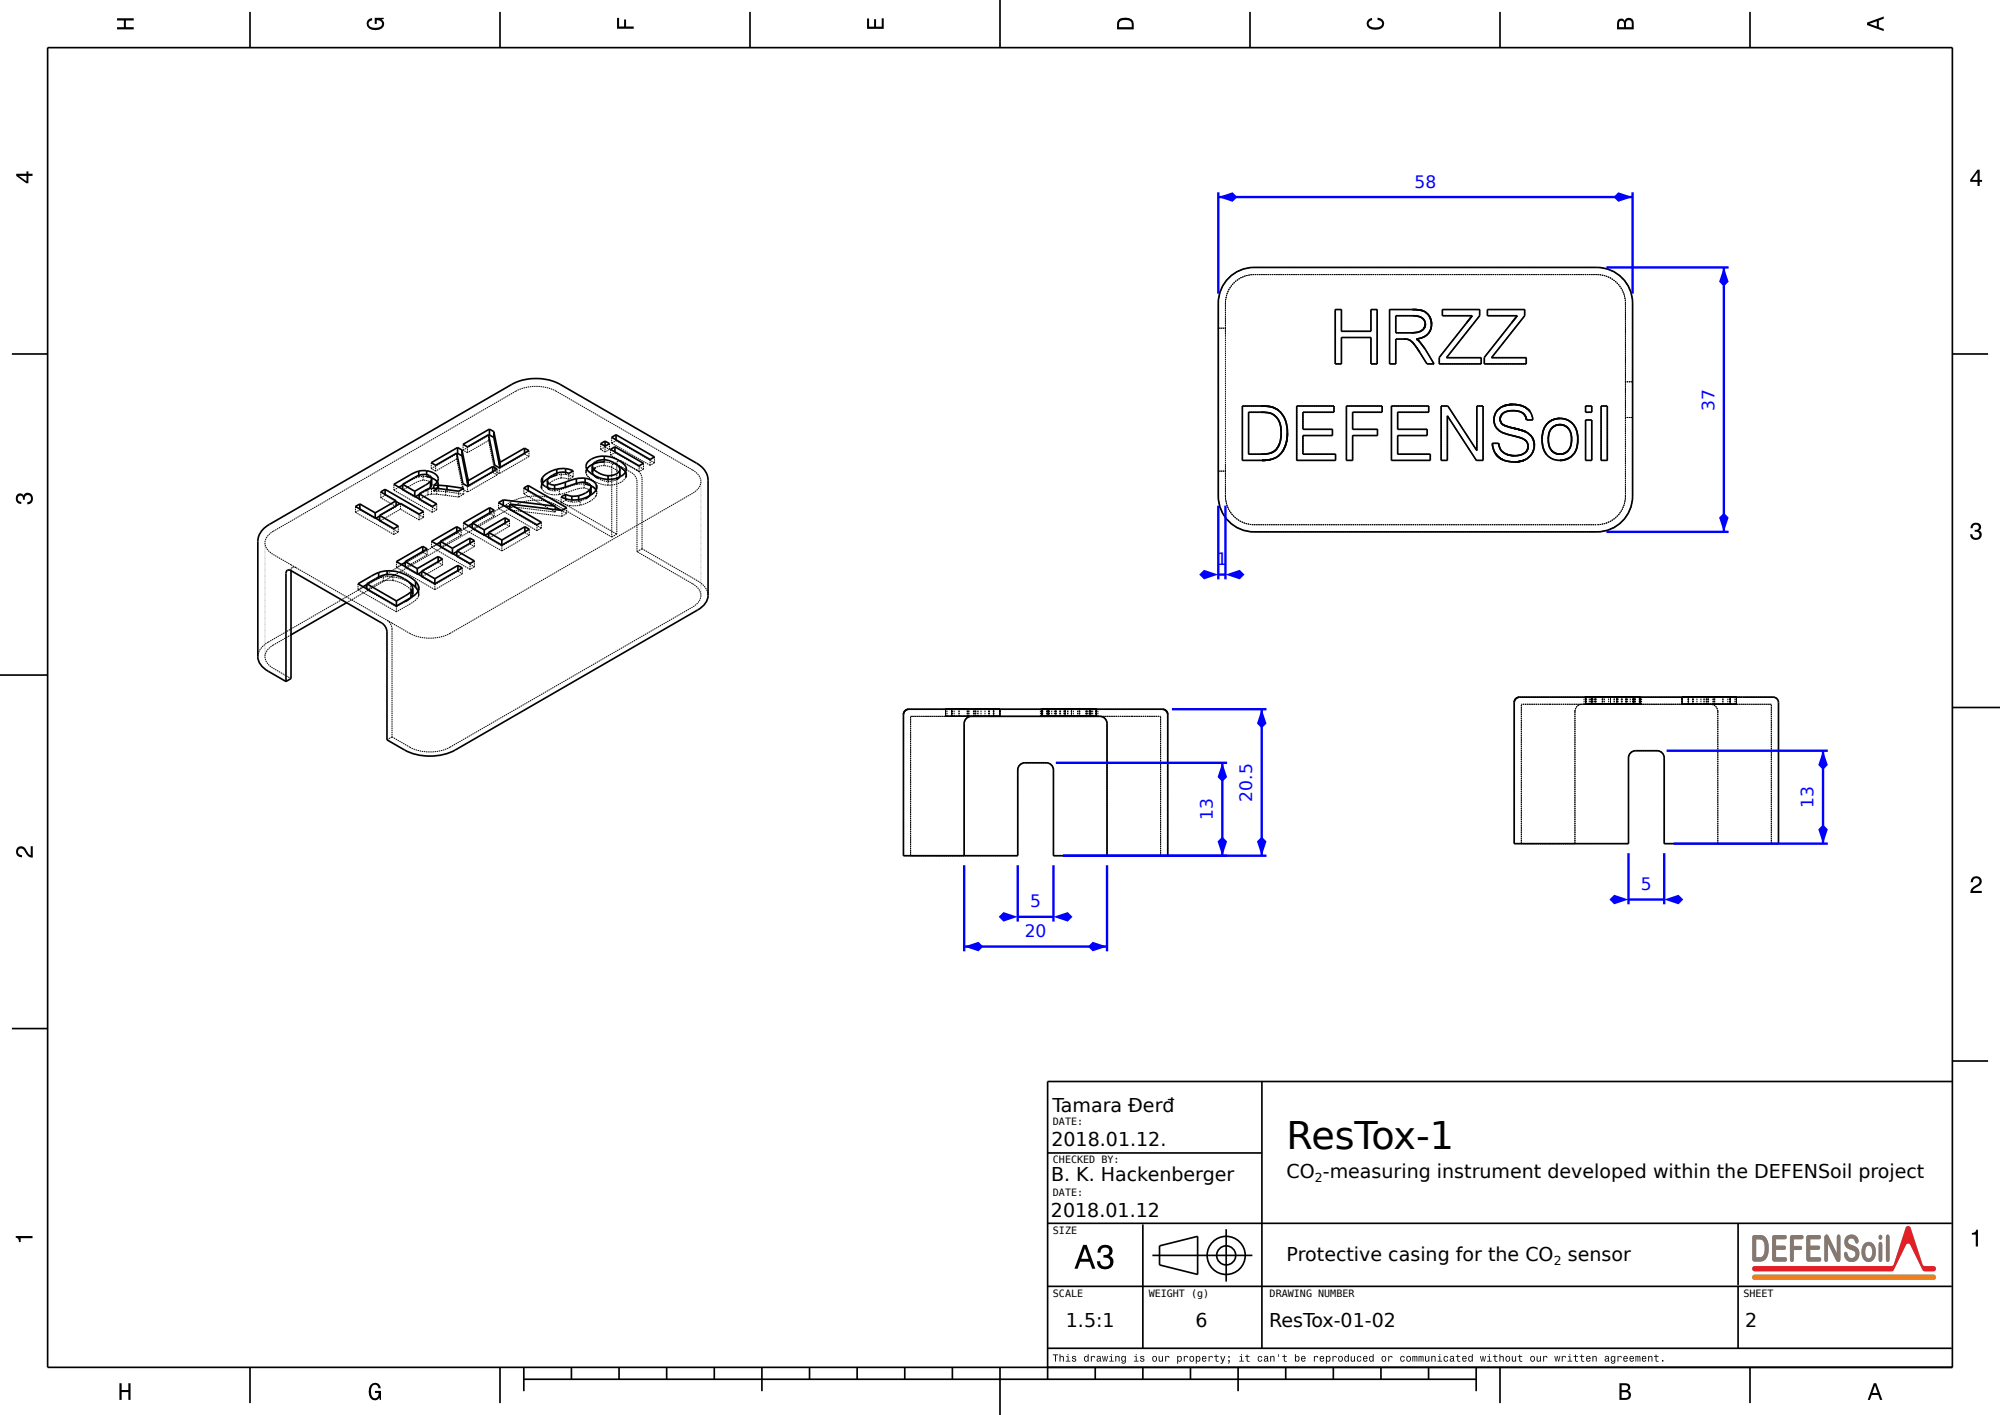
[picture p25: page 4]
Tamara Đerđ; B. K. Hackenberger; ResTox-1; DATE:; CHECKED BY:

CO2-measuring instrument developed within the DEFENSoil project

SIZE | | Protective casing for the CO2 sensor

1.5:1 | 6 | ResTox-01-02 | 2

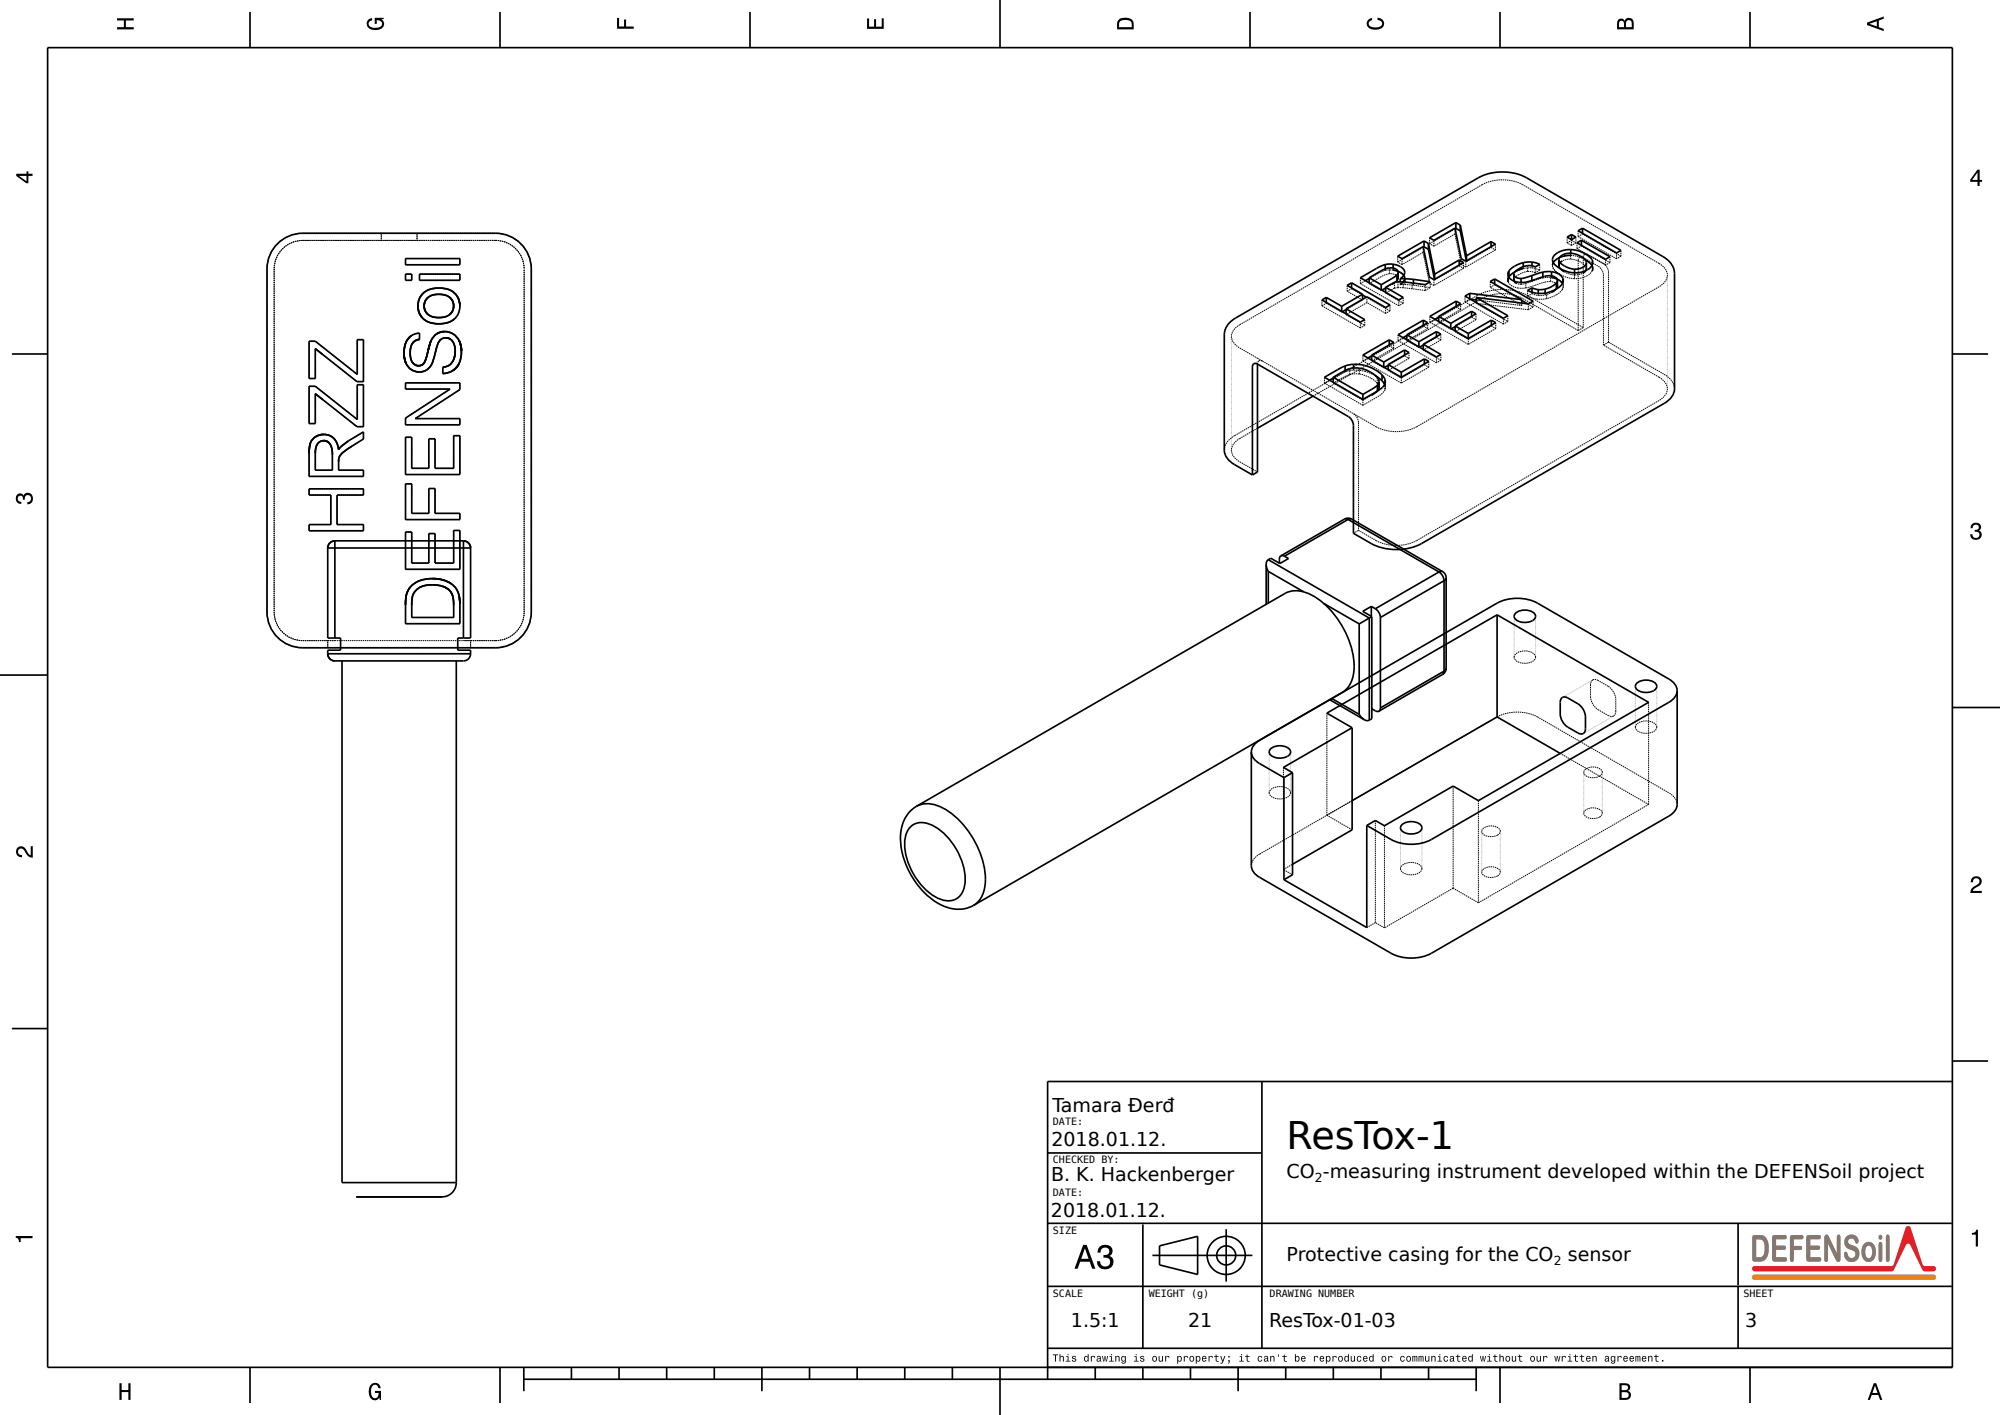
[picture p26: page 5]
Tamara Đerđ; B. K. Hackenberger; ResTox-1; DATE:; CHECKED BY:

CO2-measuring instrument developed within the DEFENSoil project

SIZE | | Protective casing for the CO2 sensor

1.5:1 | 21 | ResTox-01-03 | 3

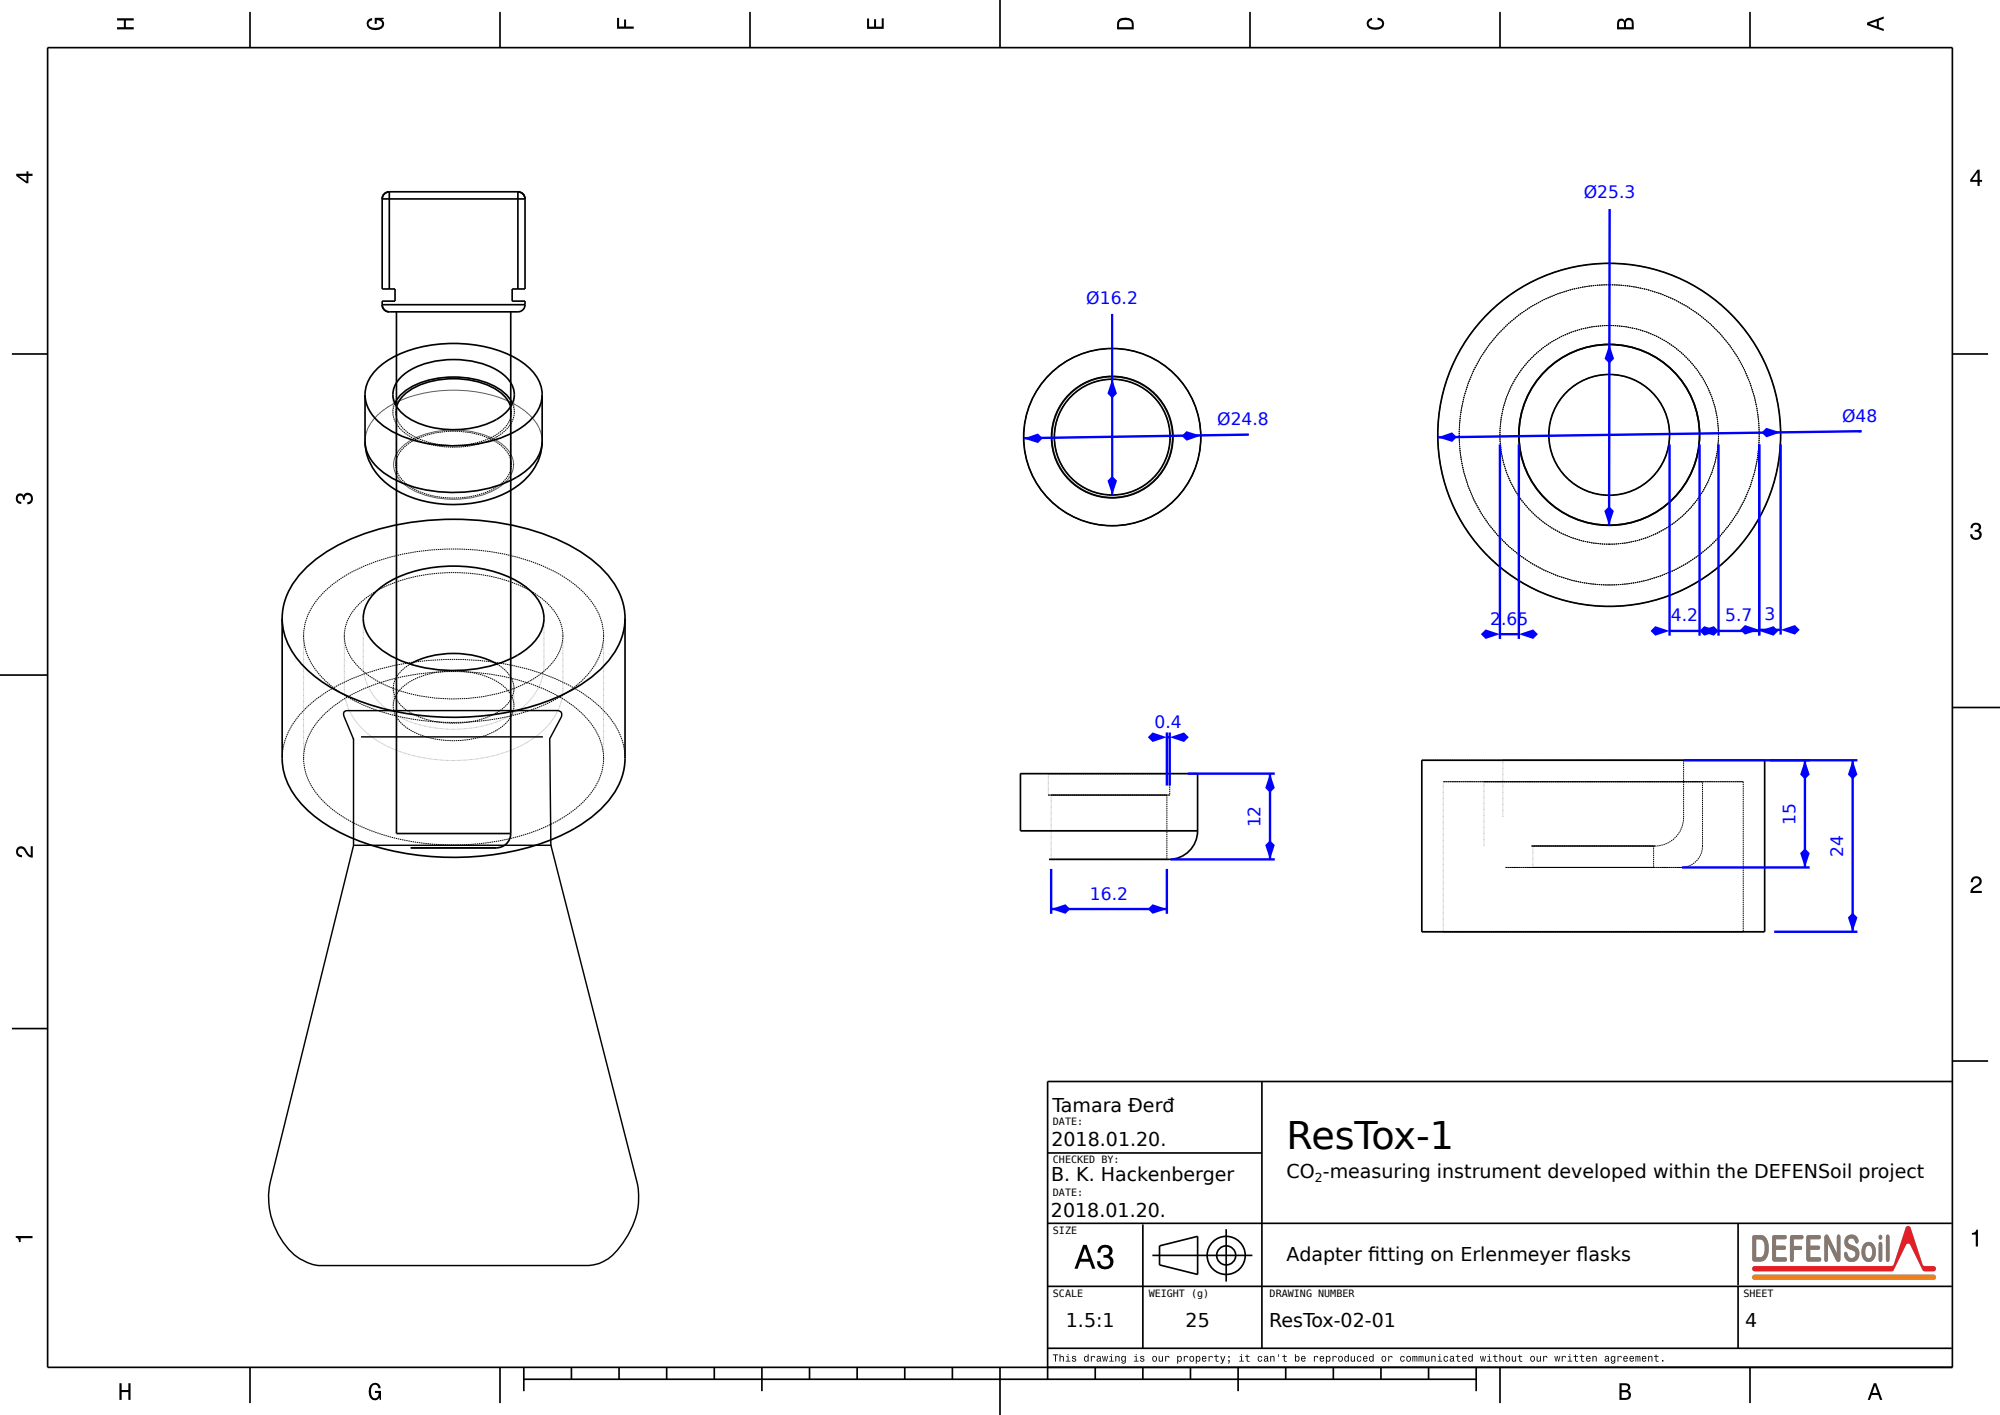
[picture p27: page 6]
Tamara Đerđ; B. K. Hackenberger; ResTox-1; DATE:; CHECKED BY:

CO2-measuring instrument developed within the DEFENSoil project

SIZE | | Adapter fitting on Erlenmeyer flasks

1.5:1 | 25 | ResTox-02-01 | 4

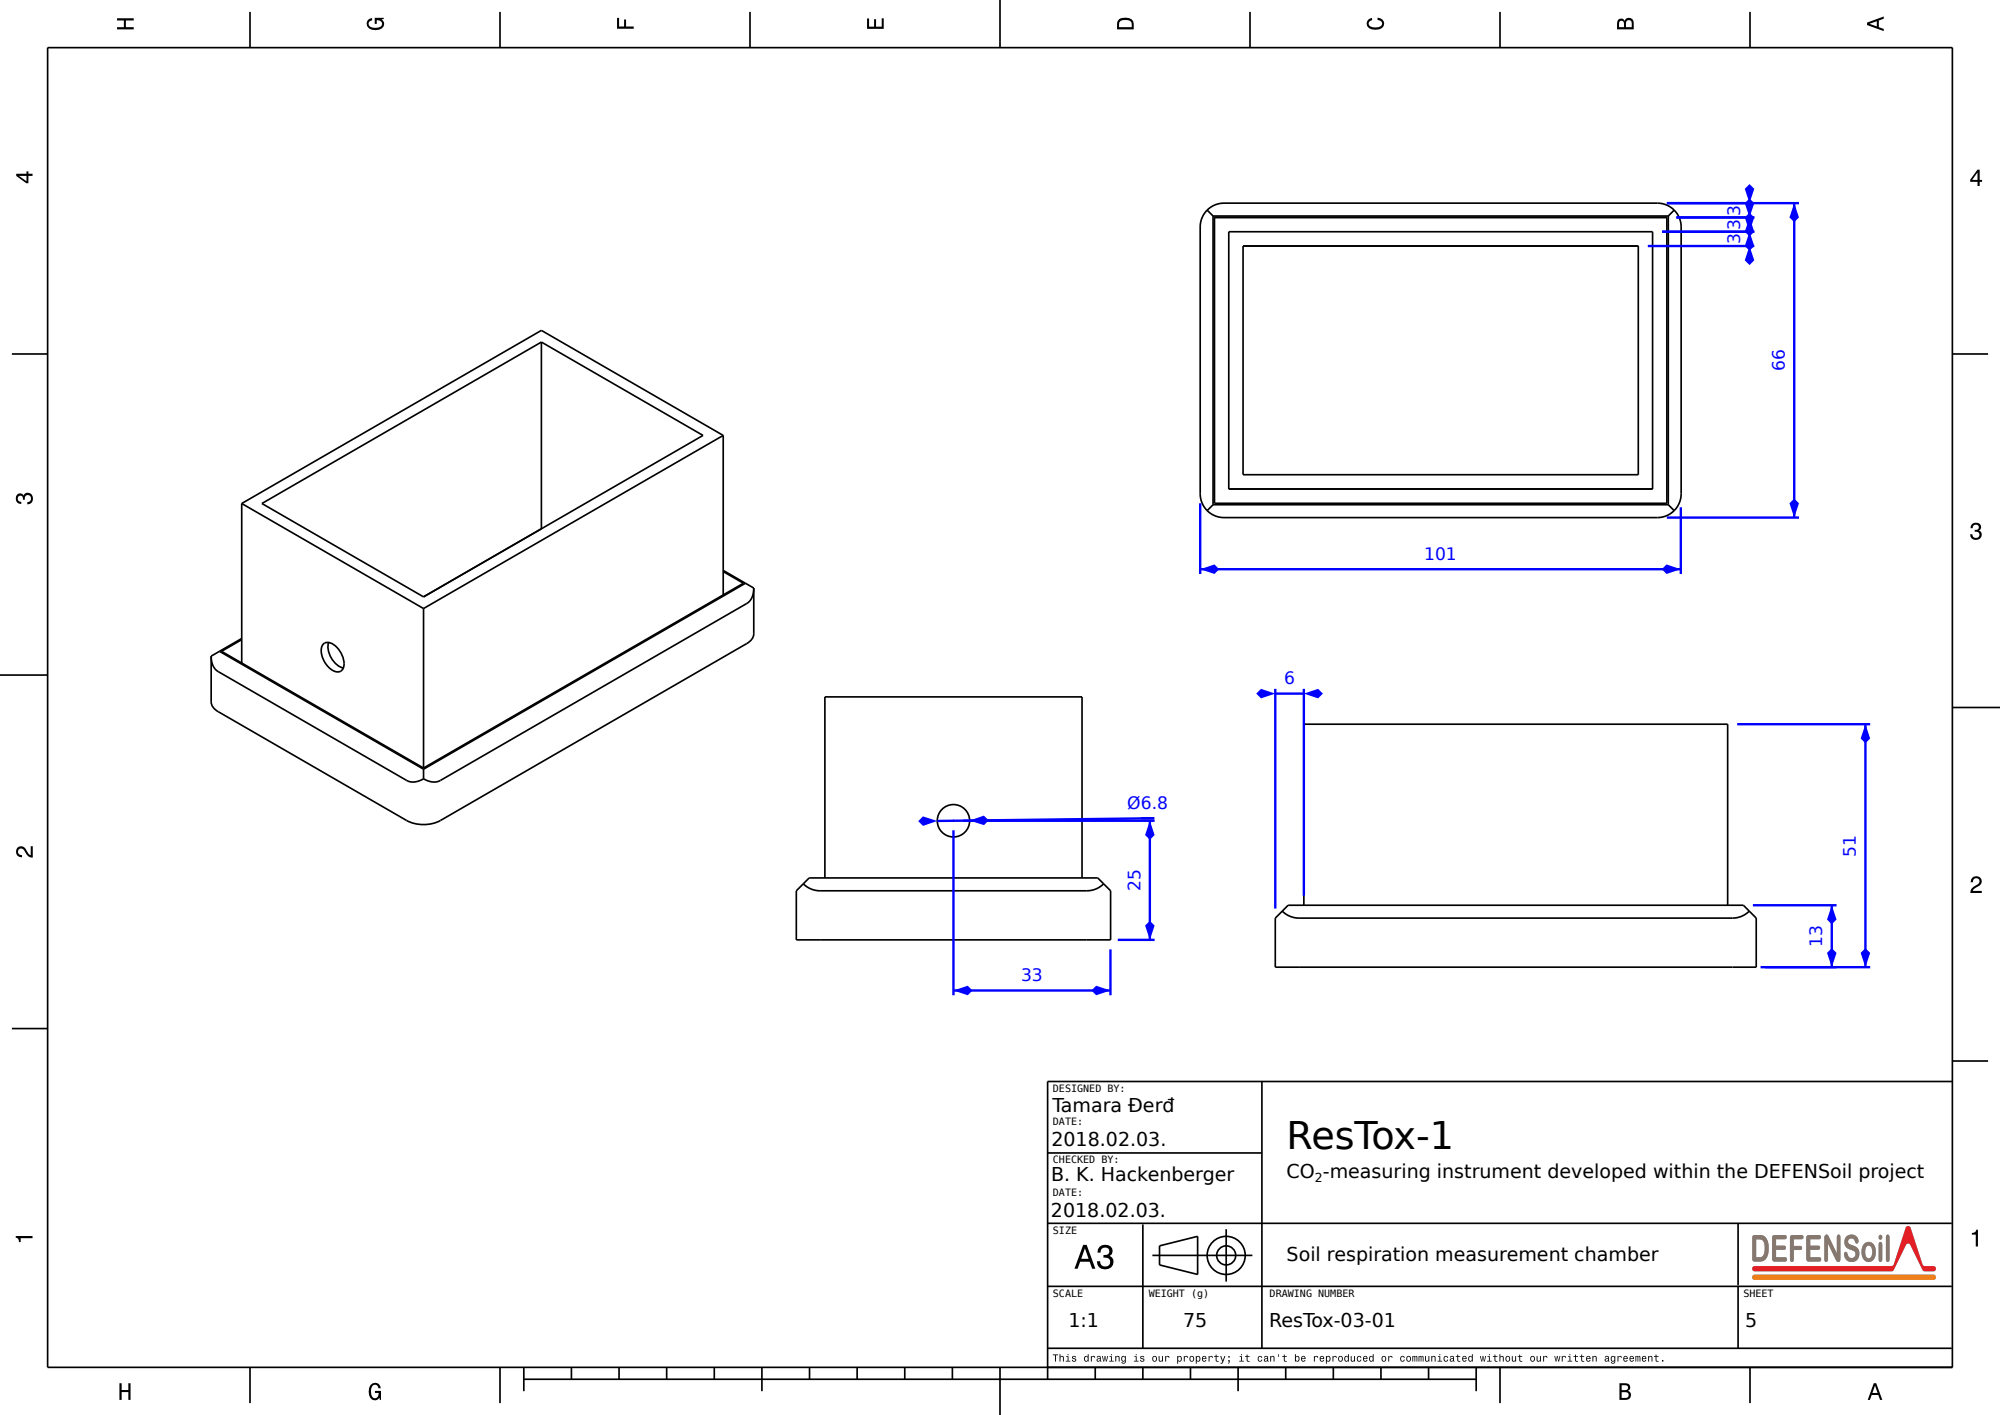
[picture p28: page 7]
Tamara Đerđ; B. K. Hackenberger; ResTox-1; DATE:; CHECKED BY:; DESIGNED BY:

CO2-measuring instrument developed within the DEFENSoil project

SIZE | | Soil respiration measurement chamber

1:1 | 75 | ResTox-03-01 | 5

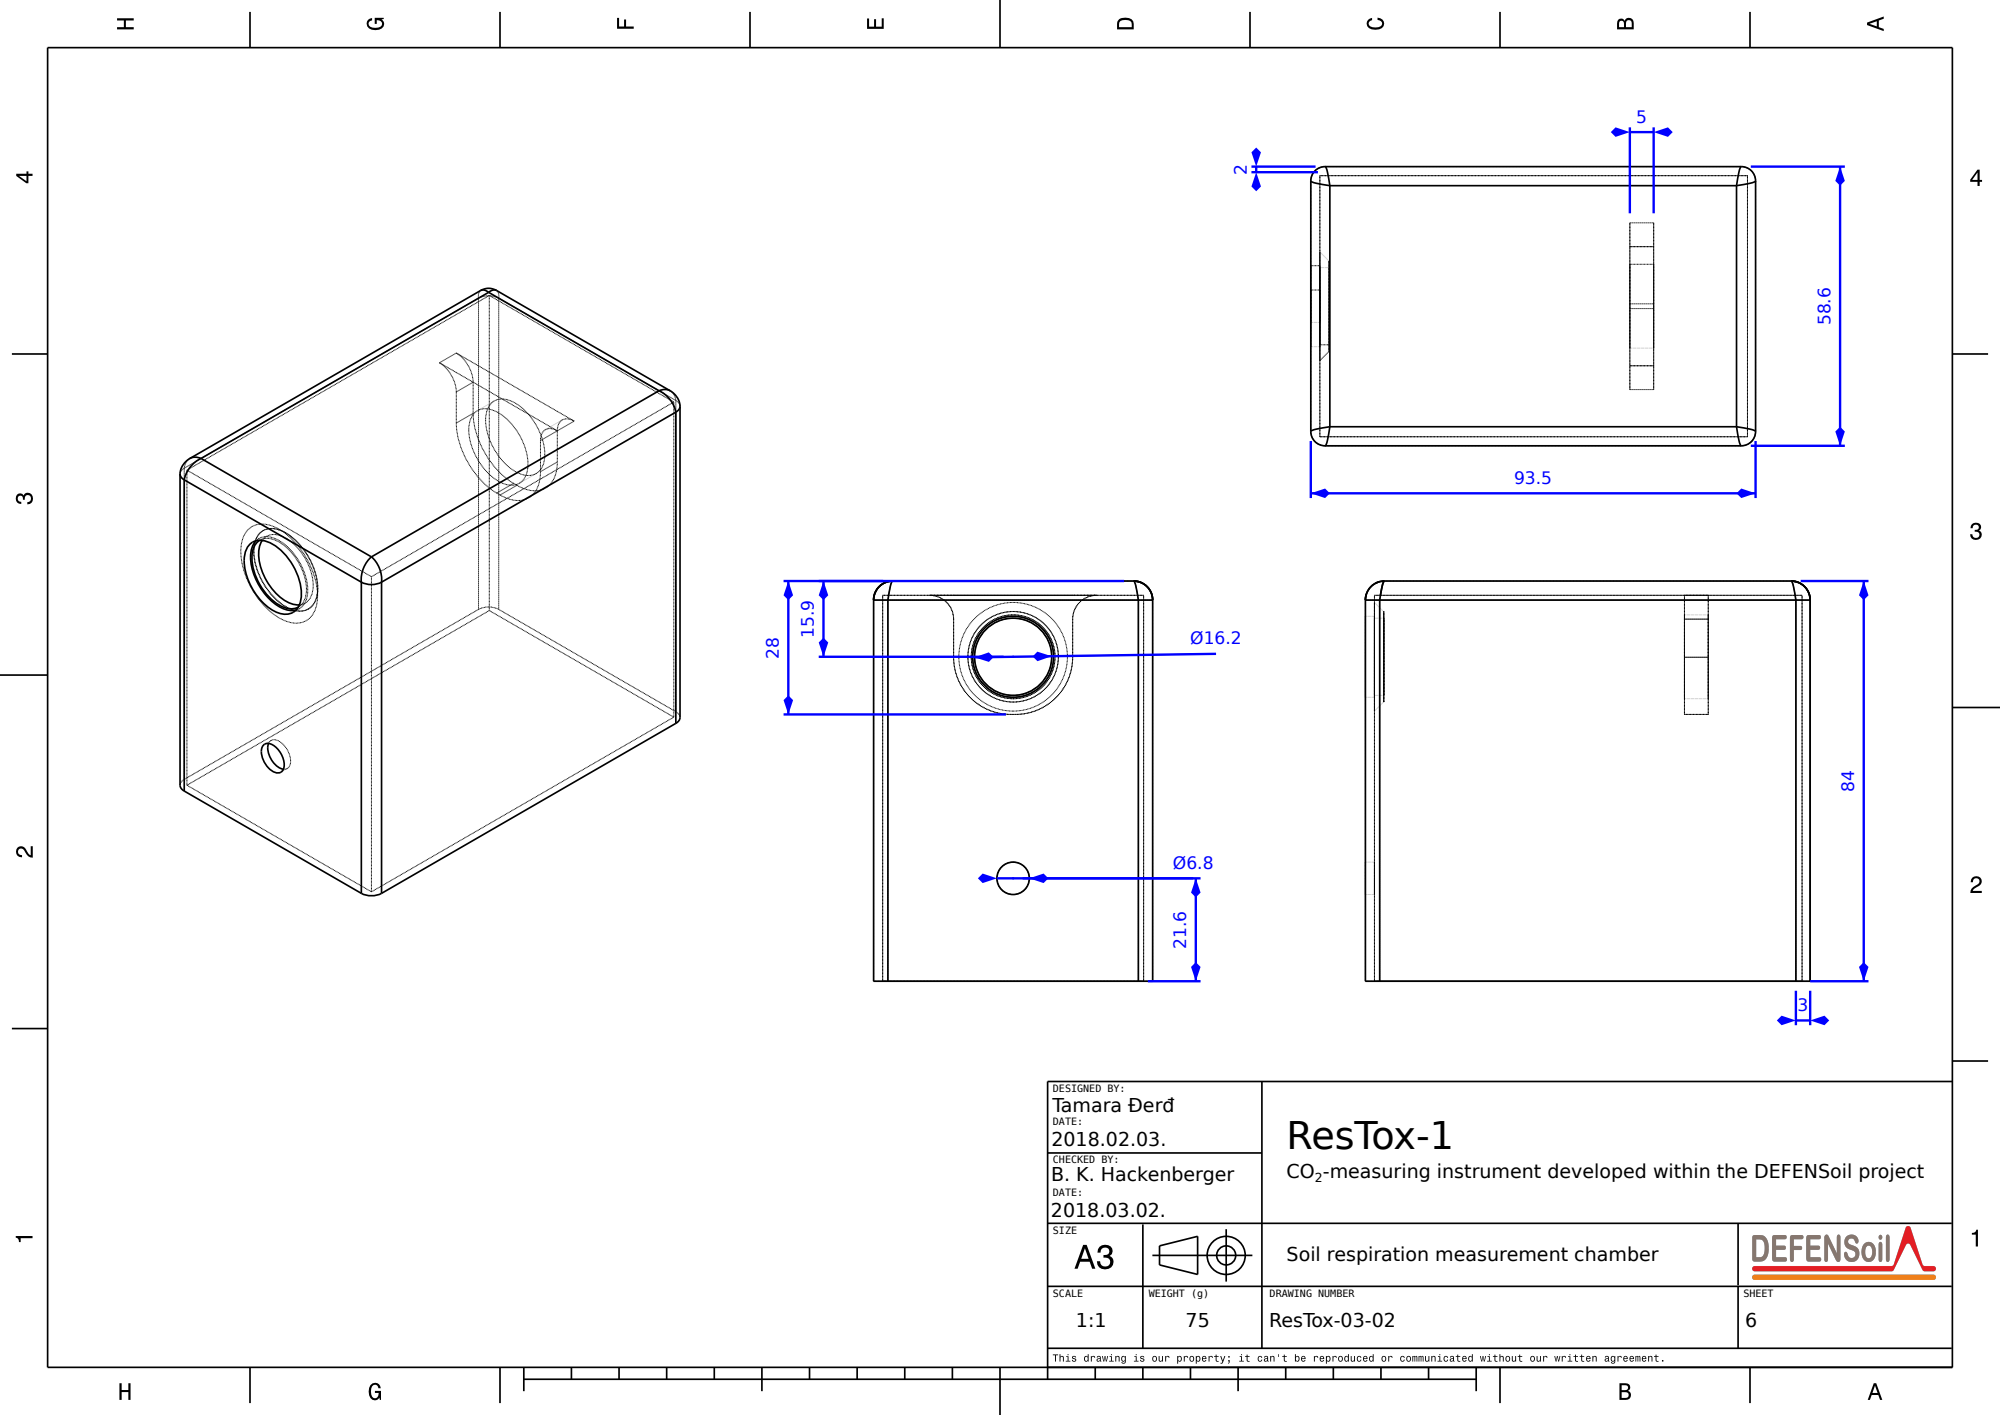
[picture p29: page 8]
Tamara Đerđ; B. K. Hackenberger; ResTox-1; DATE:; CHECKED BY:; DESIGNED BY:

CO2-measuring instrument developed within the DEFENSoil project

SIZE | | Soil respiration measurement chamber

1:1 | 75 | ResTox-03-02 | 6

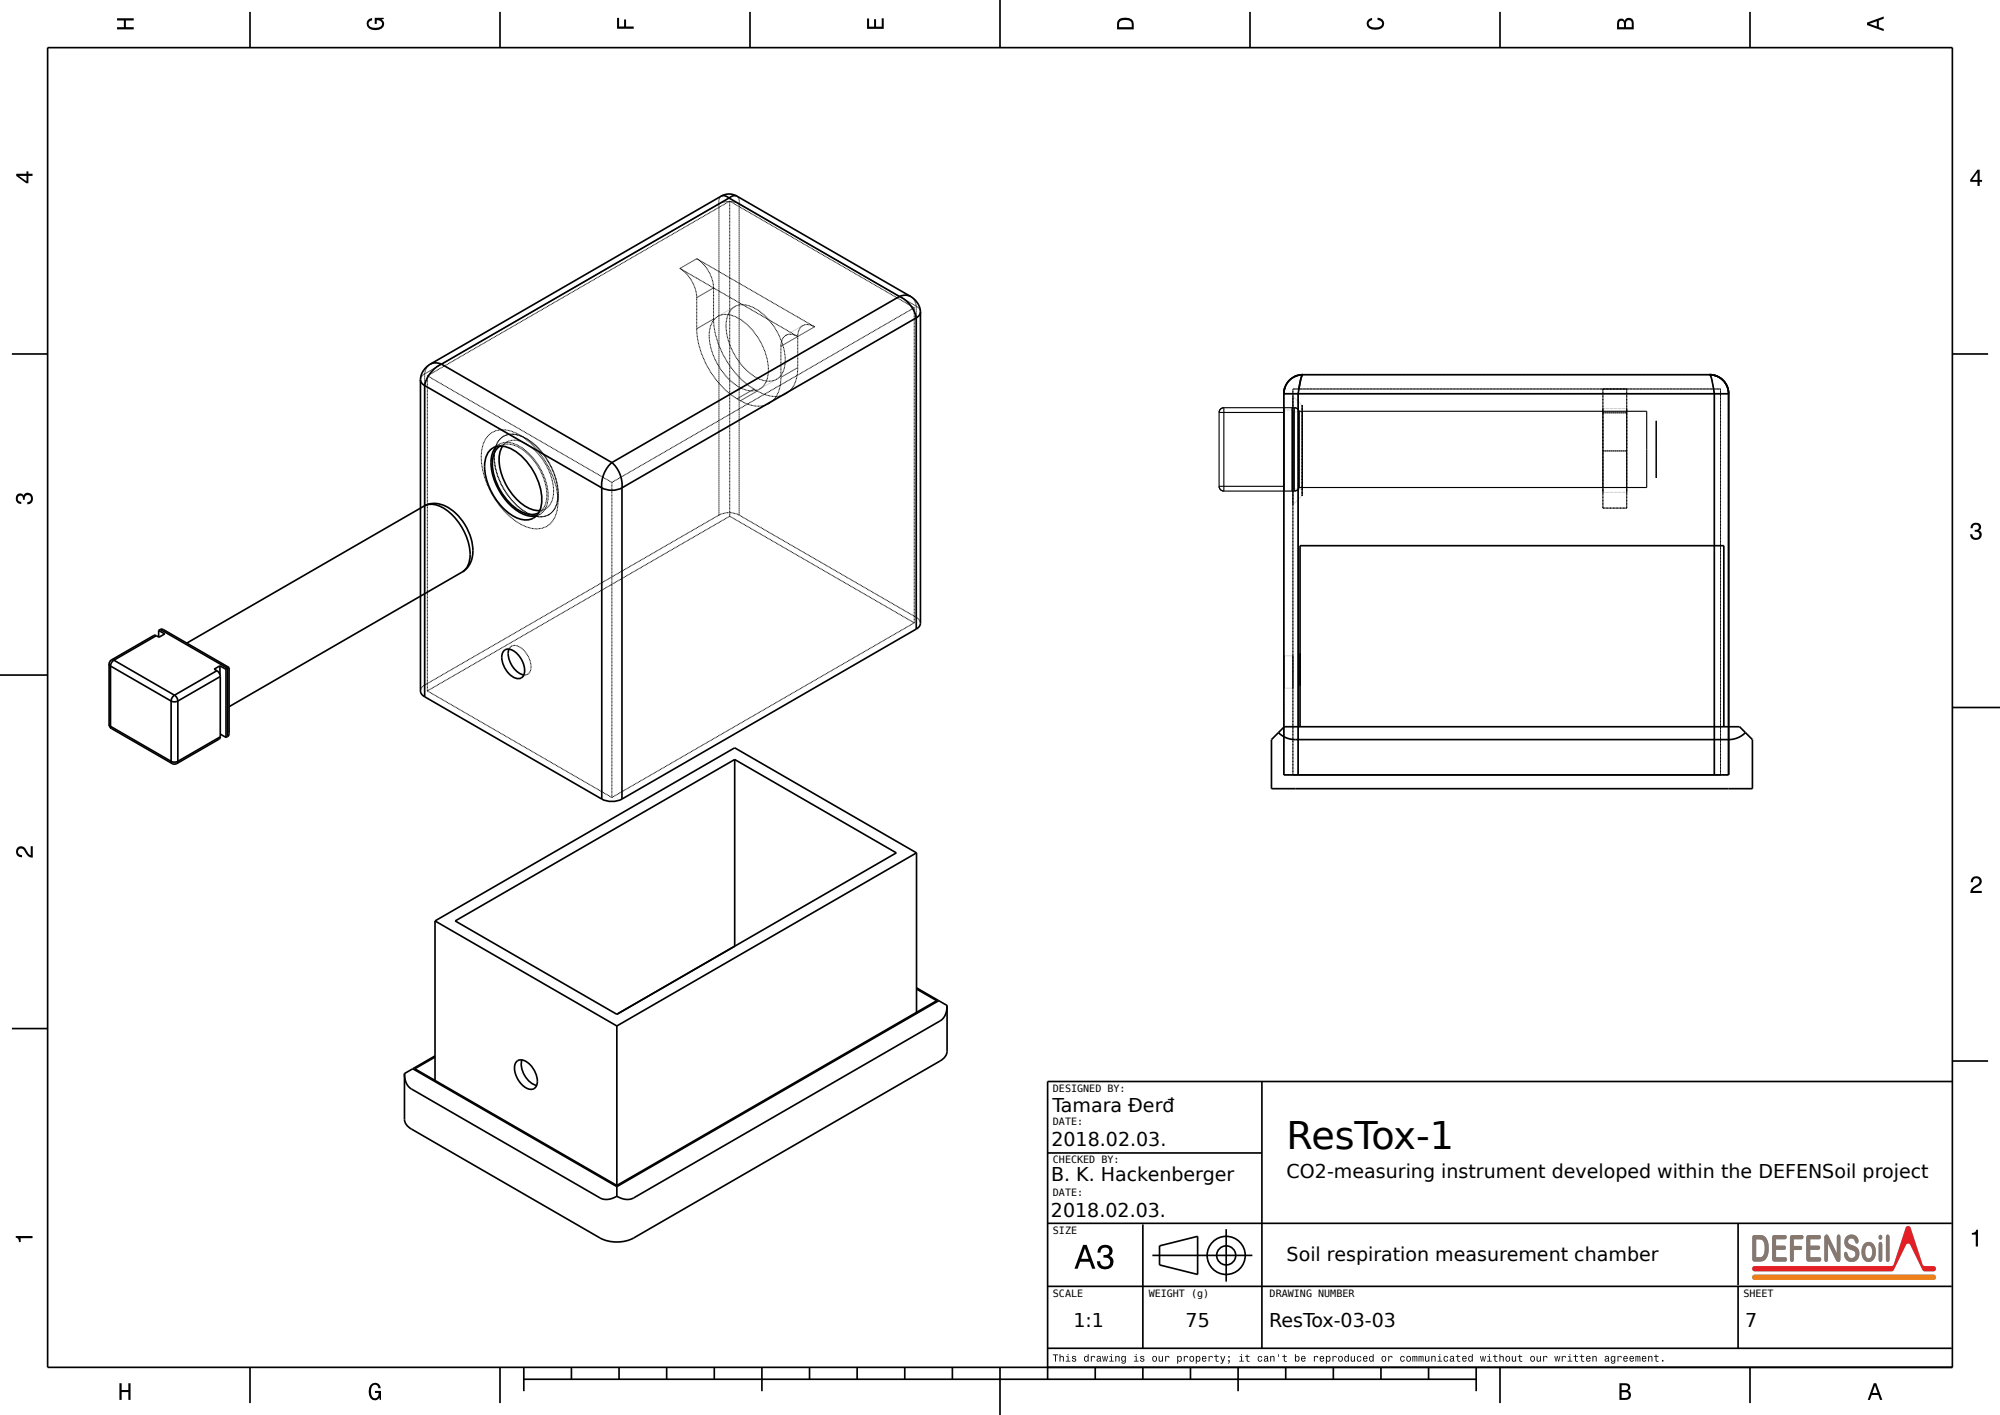
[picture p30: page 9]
Tamara Đerđ; B. K. Hackenberger; ResTox-1; DATE:; CHECKED BY:; DESIGNED BY:

CO2-measuring instrument developed within the DEFENSoil project

SIZE | | Soil respiration measurement chamber

1:1 | 75 | ResTox-03-03 | 7

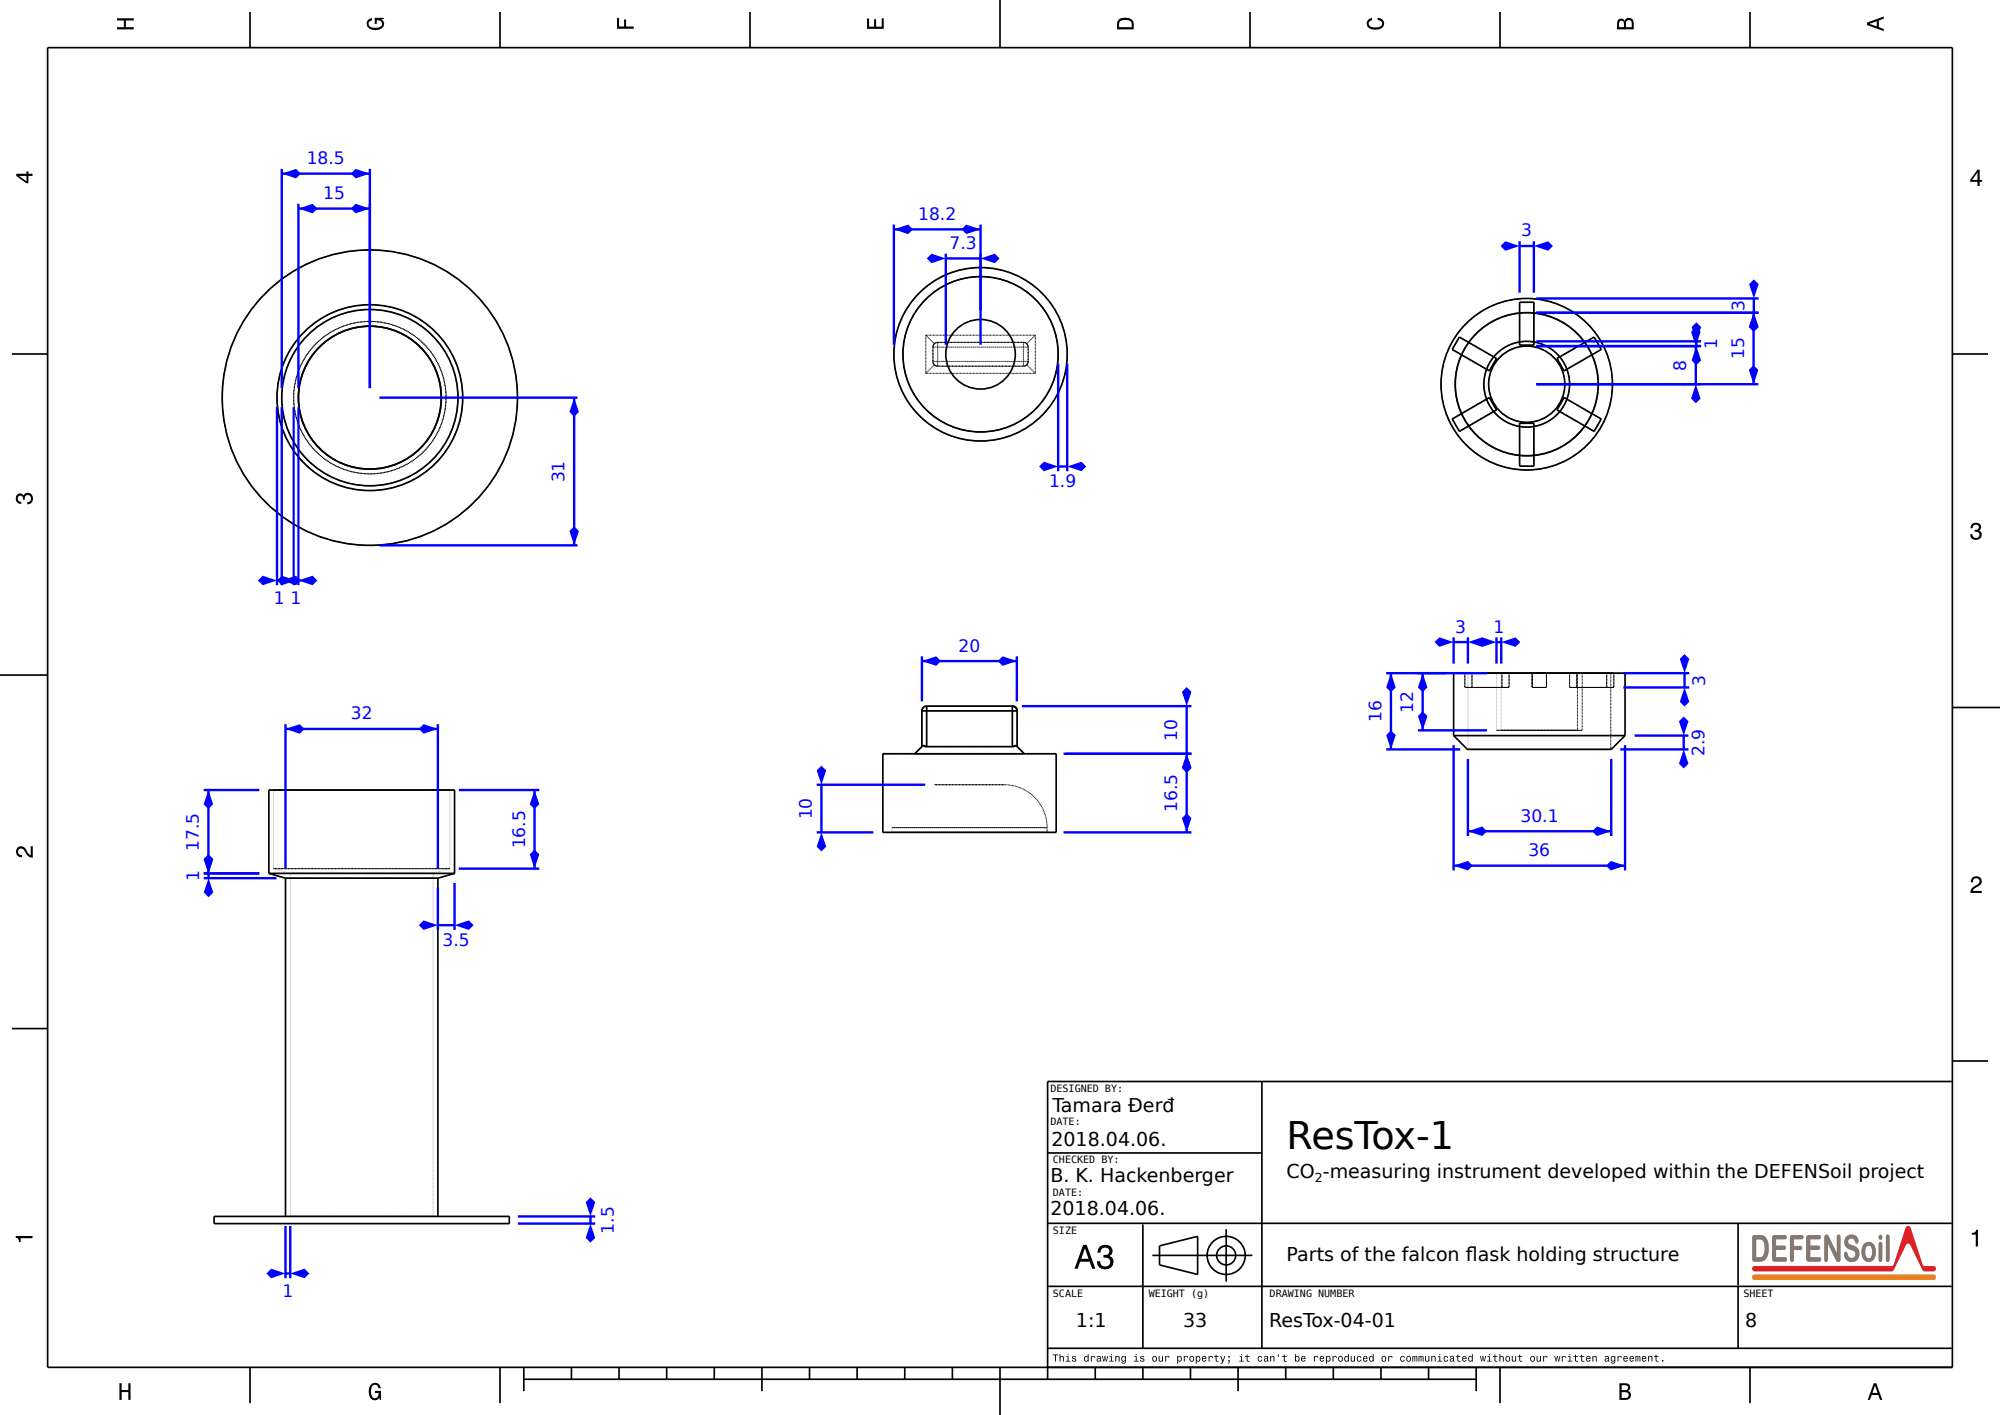
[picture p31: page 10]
Tamara Đerđ; ResTox-04-01; ResTox-1; SIZE; DATE:; CHECKED BY:; DESIGNED BY:; B. K. Hackenberger

CO2-measuring instrument developed within the DEFENSoil project

Parts of the falcon flask holding structure

Tamara Đerđ; ResTox-1; DATE:; CHECKED BY:; DESIGNED BY:; B. K. Hackenberger

CO2-measuring instrument developed within the DEFENSoil project

SIZE | | Falcon flask holding structure assembly

1:1 | 33 | ResTox-04-02 | 9

Tamara Đerđ; B. K. Hackenberger; ResTox-1; DATE:; CHECKED BY:; DESIGNED BY:

CO2-measuring instrument developed within the DEFENSoil project

SIZE | | Tube splitter

1.5:1 | 6 | ResTox-05-01 | 10

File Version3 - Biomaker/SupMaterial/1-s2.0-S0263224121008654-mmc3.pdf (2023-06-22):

A low-cost versatile system for continuous real-time respiratory activity measurement as a tool in environmental research

### Tamara Djerdj¹

### , Vesna Peršić¹

### , Davorka K. Hackenberger¹

### , Domagoj K. Hackenberger¹

### , Branimir K. Hackenberger¹,*

1
Josip Juraj Strossmayer University of Osijek, Department of Biology, Cara Hadrijana 8/A, HR-31000 Osijek, Croatia

* To whom correspondence should be addressed at Josip Juraj Strossmayer University of Osijek, Department of Biology, Cara Hadrijana 8/A, 31000

### Osijek, Croatia

### Fax: +385 31 399-939. Phone: +385 31 399-910. E-mail: hackenberger@biologija.unios.hr


### Supplementary Material S3. Wiring diagram and Arduino code

### Supplementary Material S3. Wiring diagram and Arduino code

/* RTOX metabolic rate measuring system software *
* CONNECTING THE COMPONENTS
*
* 20x4 LCD screen: VCC - 5V; GND - GND; SDA - D20; SCL - D21 *
* SEN0220 NDIR CO2 sensors (Vin - 5V; GND - GND):
* - Ref (S1): RX1 = 10; TX1 = 2;
* - Exp1 (S2): RX2 = 11; TX2 = 3;
* - Exp2 (S3): RX3 = 12; TX3 = 4;
* - Exp3 (S4): RX4 = 50; TX4 = 44; * - Exp4 (S5): RX5 = 51; TX5 = 45; * - Exp5 (S6): RX6 = 52; TX6 = 46; * - Exp6 (S7): RX7 = 53; TX7 = 47; * - Exp7 (S8): RX8 = 62; TX8 = 48;
* - Exp8 (S9): RX9 = 63; TX9 = 49;
*
* DS18B20 temperature sensor: Vin - 5V; GND; signal - D3 (4.7k resistor between 5V and D3) *
* LCD backlight switch button (push-button): D2, GND (2.2k resistor between Data and 5V)
* Manual reset push-button: 5V, GND, RESET (1k resistor between RESET and 5V)
* Photosensor: Vin - 5V; GND; A2 (10k resistor between Data and GND)
*
*/

// Software reset library for Arduino - implementing in cases of sudden CO2 concentration jumps #include <SoftReset.h>

#include <SoftwareSerial.h>

// LCD screen
#include <Wire.h>

#include <LCD.h>

#include <LiquidCrystal_I2C.h>

LiquidCrystal_I2C lcd(0x27,2,1,0,4,5,6,7,3,POSITIVE); // 0x27 is the I2C bus address for an unmodified backpack

// LCD screen backlight control
const int buttonPin = 6;
volatile int buttonState = 0; boolean light_on = true;

// Photosensor
int PHS_pin = 2;
float PHS_reading;

// Temperature
#include <DallasTemperature.h> #include <OneWire.h>

int temp_sensor = 8;
float temp = 0;

OneWire oneWirePin(temp_sensor); DallasTemperature sensors(&oneWirePin);

// Vacuum-pump control
#define RELAY 30

int data;

// Preparation of CO2-variables
// Communication with the CO2 sensors int RX1 = 10; int TX1 = 2;
int RX2 = 11; int TX2 = 3;
int RX3 = 12; int TX3 = 4;
int RX4 = 50; int TX4 = 44; int RX5 = 51; int TX5 = 45; int RX6 = 52; int TX6 = 46; int RX7 = 53; int TX7 = 47;
int RX8 = 62; int TX8 = 48;
int RX9 = 63; int TX9 = 49;

unsigned char hexdata[9] = {0xFF, 0x01, 0x86, 0x00, 0x00, 0x00, 0x00, 0x00, 0x79};

// Storing CO2 values
// Raw data
int CO2_1_r; int CO2_2_r; int CO2_3_r; int CO2_4_r; int CO2_5_r; int CO2_6_r; int CO2_7_r; int CO2_8_r; int CO2_9_r;
// Average CO2 concentration in t=0
int CO2_0_av;
// Corrected values
int CO2_1_c; int CO2_2_c; int CO2_3_c; int CO2_4_c; int CO2_5_c; int CO2_6_c; int CO2_7_c; int CO2_8_c; int CO2_9_c;
// CO2 concentration change in unit of time (s)
int v1; int v2; int v3; int v4; int v5; int v6; int v7; int v8; int v9;
// Variables used for correction of raw data
int noise; // deviation from initial value of ambient CO2 concentration
int d_S1; int d_S2; int d_S3; int d_S4; int d_S5; int d_S6; int d_S7; int d_S8; int d_S9; // sensor errors

void setup() {
Serial.begin(9600);

pinMode(RELAY, OUTPUT);

sensors.begin();

// activate LCD module
lcd.begin (20,4);
lcd.setBacklightPin(3,POSITIVE); lcd.setBacklight(HIGH);

lcd.home(); // set cursor to 0,0 lcd.print(" DEFENSoil");
lcd.setCursor(0,1);
lcd.print(" RespiroMeter");

delay(3000);

lcd.clear();

CO2_1_r = readCO2(RX1, TX1); CO2_2_r = readCO2(RX2, TX2); CO2_3_r = readCO2(RX3, TX3); CO2_4_r = readCO2(RX4, TX4); CO2_5_r = readCO2(RX5, TX5); CO2_6_r = readCO2(RX6, TX6);

CO2_7_r = readCO2(RX7, TX7);
CO2_8_r = readCO2(RX8, TX8);
CO2_9_r = readCO2(RX9, TX9);

CO2_0_av = (CO2_1_r + CO2_2_r + CO2_3_r + CO2_4_r + CO2_5_r + CO2_6_r + CO2_7_r + CO2_8_r + CO2_9_r)/9;

d_S1 = CO2_1_r - CO2_0_av;
d_S2 = CO2_2_r - CO2_0_av;
d_S3 = CO2_3_r - CO2_0_av; d_S4 = CO2_4_r - CO2_0_av; d_S5 = CO2_5_r - CO2_0_av; d_S6 = CO2_6_r - CO2_0_av; d_S7 = CO2_7_r - CO2_0_av; d_S8 = CO2_8_r - CO2_0_av; d_S9 = CO2_9_r - CO2_0_av; }

void loop() {
CO2_1_r = readCO2(RX1, TX1); CO2_2_r = readCO2(RX2, TX2); CO2_3_r = readCO2(RX3, TX3); CO2_4_r = readCO2(RX4, TX4); CO2_5_r = readCO2(RX5, TX5); CO2_6_r = readCO2(RX6, TX6); CO2_7_r = readCO2(RX7, TX7); CO2_8_r = readCO2(RX8, TX8); CO2_9_r = readCO2(RX9, TX9);

noise = CO2_1_r - d_S1 - CO2_0_av;

CO2_1_c = CO2_1_r - d_S1 - noise; CO2_2_c = CO2_2_r - d_S2 - noise; CO2_3_c = CO2_3_r - d_S3 - noise; CO2_4_c = CO2_4_r - d_S4 - noise; CO2_5_c = CO2_5_r - d_S5 - noise; CO2_6_c = CO2_6_r - d_S6 - noise; CO2_7_c = CO2_7_r - d_S7 - noise; CO2_8_c = CO2_8_r - d_S8 - noise; CO2_9_c = CO2_9_r - d_S9 - noise;

PHS_reading = analogRead(PHS_pin);

sensors.requestTemperatures();
temp = sensors.getTempCByIndex(0);

// lcd.clear();
lcd.setCursor(2,0);
lcd.print("1:");
lcd.setCursor(4,0);
lcd.print(" ");
lcd.setCursor(4,0);
lcd.print(CO2_2_c);
lcd.setCursor(11,0);
lcd.print("2:");
lcd.setCursor(13,0);
lcd.print(" ");

lcd.setCursor(13,0);
lcd.print(CO2_3_c);
lcd.setCursor(2,1);
lcd.print("3:");
lcd.setCursor(4,1);
lcd.print(" ");
lcd.setCursor(4,1);
lcd.print(CO2_4_c);
lcd.setCursor(11,1);
lcd.print("4:");
lcd.setCursor(13,1);
lcd.print(" ");
lcd.setCursor(13,1);
lcd.print(CO2_5_c);
lcd.setCursor(2,2);
lcd.print("5:");
lcd.setCursor(4,2);
lcd.print(" ");
lcd.setCursor(4,2);
lcd.print(CO2_6_c);
lcd.setCursor(11,2);
lcd.print("6:");
lcd.setCursor(13,2);
lcd.print(" ");
lcd.setCursor(13,2);
lcd.print(CO2_7_c);
lcd.setCursor(2,3);
lcd.print("7:");
lcd.setCursor(4,3);
lcd.print(" ");
lcd.setCursor(4,3);
lcd.print(CO2_8_c);
lcd.setCursor(11,3);
lcd.print("8:");
lcd.setCursor(13,3);
lcd.print(" ");
lcd.setCursor(13,3);
lcd.print(CO2_9_c);

if(Serial.available()>0){
data=Serial.read();
if(data==1){digitalWrite(RELAY, 1);} else if(data==0){digitalWrite(RELAY, 0);} else if(data==2){
Serial.print(CO2_1_r);
Serial.print(";");
Serial.print(CO2_1_c);
Serial.print(";");
Serial.print(noise);
Serial.print(";");
Serial.print(d_S1);
Serial.print(";");
Serial.print(CO2_2_r);
Serial.print(";");
Serial.print(CO2_2_c);
Serial.print(";");
Serial.print(d_S2);
Serial.print(";");
Serial.print(CO2_3_r);

Serial.print(";");
Serial.print(CO2_3_c);
Serial.print(";");
Serial.print(d_S3);
Serial.print(";");
Serial.print(CO2_4_r);
Serial.print(";");
Serial.print(CO2_4_c);
Serial.print(";");
Serial.print(d_S4);
Serial.print(";");
Serial.print(CO2_5_r);
Serial.print(";");
Serial.print(CO2_5_c);
Serial.print(";");
Serial.print(d_S5);
Serial.print(";");
Serial.print(CO2_6_r);
Serial.print(";");
Serial.print(CO2_6_c);
Serial.print(";");
Serial.print(d_S6);
Serial.print(";");
Serial.print(CO2_7_r);
Serial.print(";");
Serial.print(CO2_7_c);
Serial.print(";");
Serial.print(d_S7);
Serial.print(";");
Serial.print(CO2_8_r);
Serial.print(";");
Serial.print(CO2_8_c);
Serial.print(";");
Serial.print(d_S8);
Serial.print(";");
Serial.print(CO2_9_r);
Serial.print(";");
Serial.print(CO2_9_c);
Serial.print(";");
Serial.print(d_S9);
Serial.print(";");
Serial.print(PHS_reading); Serial.print(";");
Serial.println(temp);
}
}

delay(900);
}

int readCO2(int RX, int TX) { SoftwareSerial mySerial(RX, TX);

mySerial.begin(9600);

mySerial.write(hexdata, 9); delay(10);

for (int i = 0, j = 0; i < 9; i++)

{
if (mySerial.available() > 0) {
long hi, lo, CO2;
int ch = mySerial.read();

if (i == 2) {
hi = ch; //High concentration }
if (i == 3) {
lo = ch; //Low concentration
}
if (i == 8) {
CO2 = hi * 256 + lo; //CO2 concentration return(CO2);
}
}
}

mySerial.end();
}

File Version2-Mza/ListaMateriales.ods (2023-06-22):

Electronica |  |  | Mendoza |  |  | Buenos Aires | Taller
 | Componente | Cantidad | Proveedor 1 | Costo Aprox | Comentario | Proveedor 2
 | Sensor CO2 MH-Z19 | 1 | https://tienda.ityt.com.ar/gas/9736-mh-z19b-sensor-infrarrojo-co2-modelo-discontinuado-solo-a-pedido-itytarg.html?search_query=CO2&results=8 | 7900 | El original es marca Winsen pero hay muchas copias | https://articulo.mercadolibre.com.ar/MLA-933913672-sensor-digital-co2-mh-z19c-dioxido-de-carbono-infrarrojo-hob-_JM?matt_tool=56318942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 | x
 | DSB18B20 Temp sensor | 1 | https://tienda.ityt.com.ar/temperatura/7278-sensor-sonda-temperatura-ds18b20-cable-3m-arduino-itytarg.html?search_query=temperatura&results=1685 | 900
 | Sensor de humedad suelo capacitivo | 1 | https://tienda.ityt.com.ar/humedad/6547-sensor-capacitivo-analogico-de-humedad-suelo-v12-higrometro-itytarg.html?search_query=humedad+capacitivo&results=203 | 500
 | Bluetooth HC-05 | 1 | https://tienda.ityt.com.ar/modulo-bluetooth/213-modulo-hc-05-hc05-bluetooth-maestro-esclavo-arduino-itytarg.html?search_query=bluetooth&results=132 | 1350 |  |  | x
 | Arduino UNO | 1 | https://tienda.ityt.com.ar/placas-base-arduino/11339-arduino-uno-r3-atmega328p-smd-ch340g-c-cable-itytarg.html?search_query=arduino+uno&results=891 | 1320 |  |  | x
 | Arduino UNO protoboard | 1 | https://tienda.ityt.com.ar/sin-catalogar/205-protoshield-uno-con-syb-170-protoboard-arduino-itytarg.html?search_query=arduino+uno+protoboard&results=934 | 350 |  |  | x
 | Botón calibración | 1 |  |  | Se consigue en cualquier casa de electrónica |  | x
 | Resitencia 4.7kOhm | 1 |  |  | Se consigue en cualquier casa de electrónica |  | x
 | LCD 16x2 I2C | 1 | https://tienda.ityt.com.ar/display-lcd-caracter/1742-display-lcd-1602-hd44780-backlight-azul-16x2-c-i2c-itytarg.html?search_query=ldc+16x2+i2c&results=278 | 850 |  |  | x
 | Cables conectores | 1 | https://tienda.ityt.com.ar/cable-dupont/2970-40-cables-macho-hembra-20cm-premium-dupont-arduino-itytarg.html?search_query=cables+dupont&results=302 | 390 |  |  | x
 | Conector GX12 4 pin | 1 | https://tienda.ityt.com.ar/sin-catalogar/6970-gx12-conector-4-pin-circular-rosca-12mm-macho-y-hembra-chasis-itytarg.html?search_query=conector+gx&results=714 | 420 |  |  | x
 | Conector GX12 3 pin | 2 | https://tienda.ityt.com.ar/sin-catalogar/6969-gx12-conector-3-pin-circular-rosca-12mm-macho-y-hembra-chasis-itytarg.html?search_query=conector+gx&results=714 | 815 |  |  | x
Cámara y carcaza
 | Caño sanitario 110mm x 20cm | 1 |  |  | Se consigue en cualquier ferretería
 | Tapa caño sanitario 110mm | 1 |  |  | Se consigue en cualquier ferretería
 | Caja | 1 | https://articulo.mercadolibre.com.ar/MLA-909839661-roker-caja-paso-exterior-ip65-115x115x081-pr99881-_JM?matt_tool=92724942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 | 550 | Se puede conseguir en cualquier casa de electricidad
Partes impresas
 | Base para Sensor CO2 | 1 |  |  |  |  | x
 | Base para Arduino Uno | 1 |  |  |  |  | x
 | Base para LCD | 1 |  |  |  |  | x
 |  |  |  | 15345

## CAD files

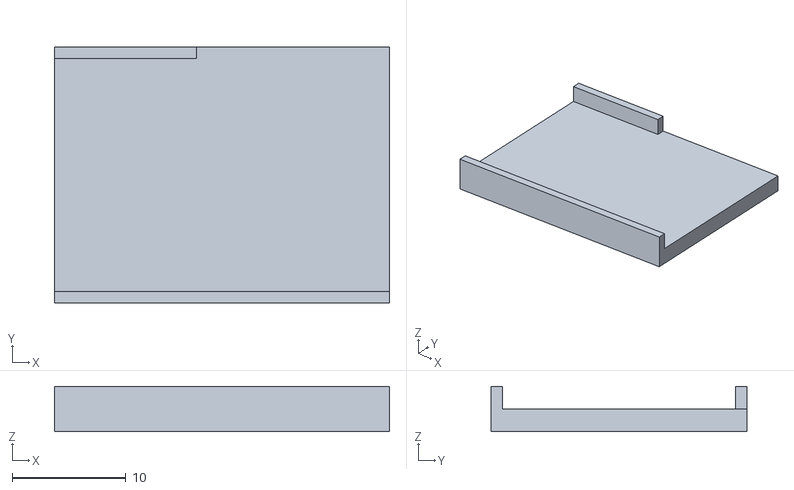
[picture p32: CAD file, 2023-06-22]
Version2-Mza/Hardware/STL/mz_holder_soil_resp.stl
29.5 x 22.5 x 4.00

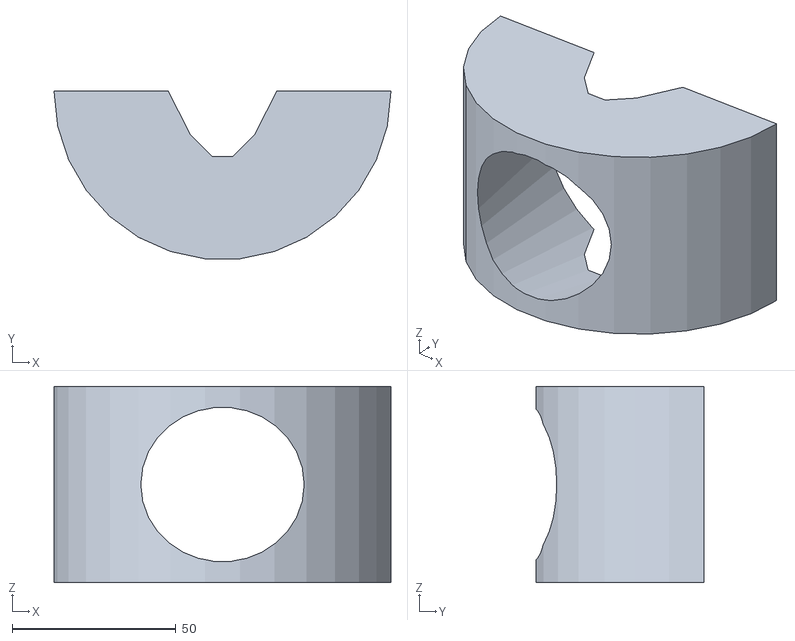
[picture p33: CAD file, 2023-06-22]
Version3 - Biomaker/vase holder.stl
103.0 x 51.2 x 60.0

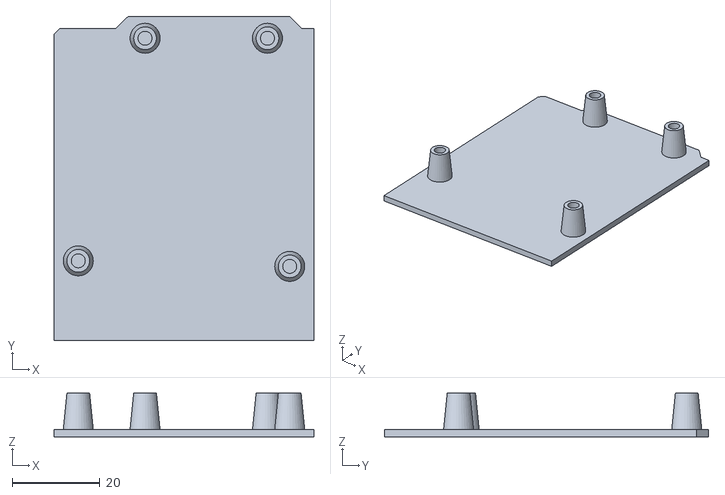
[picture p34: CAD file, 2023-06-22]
Version2-Mza/Hardware/STL/uno_stand.stl
59.3 x 74.1 x 10.0

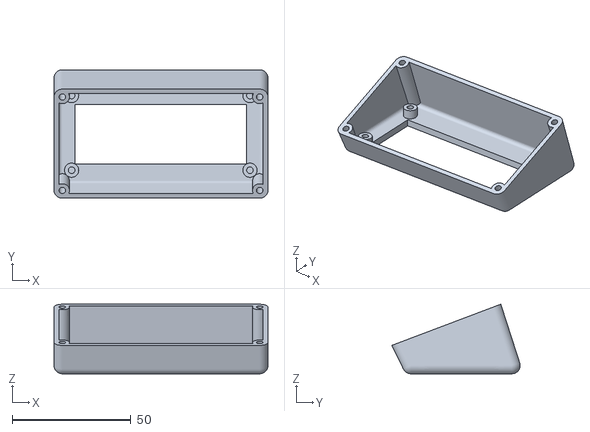
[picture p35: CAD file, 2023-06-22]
Version2-Mza/Hardware/STL/lcd_hood_internal_fix.stl
90.0 x 54.0 x 29.3

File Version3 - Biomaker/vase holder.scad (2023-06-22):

difference(){
cylinder(h=60,d=103,center=true);
translate([0,30,0])
    cube([120,60,100],center=true);
rotate([-90,0,0])
    translate([0,0,-52])
#cylinder(h=60,d1=47,d2=72);
}

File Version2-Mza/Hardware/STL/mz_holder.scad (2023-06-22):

caja_x=42;
caja_y=62;
caja_z=22;
mz_x=27;
mz_y=20;
mz_z=9;
mz_hole_x=3;
e=2;

difference(){
union(){
cube([caja_x,caja_y,e]);
 translate([(caja_x-mz_x-2*mz_hole_x)/2,(caja_y-mz_y-2*e)/2,0])
 cube([mz_x+2*mz_hole_x,mz_y+2*e,caja_z-mz_z-2*e]);
translate([0,0,caja_z-mz_z-2*e])
difference(){
translate([(caja_x-mz_x-2*mz_hole_x)/2,(caja_y-mz_y-2*e)/2,0])
 cube([mz_x+2*mz_hole_x,mz_y+2*e,e*2]);
translate([0,(caja_y-mz_y+2*e-2*e)/2,e])
    cube([caja_x,mz_y,caja_z]);
translate([e,0,e])
    cube([caja_x/2,caja_y/2,2*e]);   
}}
translate([2*e,caja_y/2-(mz_y-2*e)/2,0])  
cube([mz_hole_x,mz_y-2*e,caja_z]);
    translate([4*e+mz_x,caja_y/2-(mz_y-2*e)/2,0])  
cube([mz_hole_x,mz_y-2*e,caja_z]);
translate([2*e,2*e,0])
#cylinder(h=10,d=3,center=true);
translate([caja_x-2*e,2*e,0])
#cylinder(h=10,d=3,center=true);
translate([caja_x-2*e,caja_y-2*e,0])
#cylinder(h=10,d=3,center=true);
translate([2*e,caja_y-2*e,0])
#cylinder(h=10,d=3,center=true);


}

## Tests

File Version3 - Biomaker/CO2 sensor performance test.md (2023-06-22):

# CO2 sensor performance test

We wanted to evaluate the performance of different CO2 sensors to be used into a soil respiration chamber. You can find more info about [our prototype](https://gitlab.com/nanocastro/camara-respiracion-suelo/-/wikis/home) here and several more version on [Hackteria wiki.](https://www.hackteria.org/wiki/CO2_Soil_Respiration_Chamber#URO.C5.A0_new_CO2_soil_chambers)

Our test doesn't include CO2 standards so we are not looking at absolute values but only the behavior of the different sensors in different situations: exposed to ambient air, inside an empty closed chamber and inside the same chamber but in the presence of a rewetted soil sample.

## Sensors

We used three different CO2 sensors  

| Sensor          | Technology                                                   | Aprox Price (USD) | Datasheet                                                    | Code Reference                                               |
| --------------- | ------------------------------------------------------------ | ----------------- | ------------------------------------------------------------ | ------------------------------------------------------------ |
| Winsen MH-Z16   | [NDIR](https://en.wikipedia.org/wiki/Nondispersive_infrared_sensor) | 80                | [MH-Z16](https://www.winsen-sensor.com/d/files/MH-Z16.pdf)   | [Arduino example](https://wiki.dfrobot.com/Infrared_CO2_Sensor_0-50000ppm_SKU__SEN0220) |
| Winsen MH-Z19   | NDIR                                                         | 30                | [MH-Z19](https://www.winsen-sensor.com/d/files/infrared-gas-sensor/ndir-co2-sensor/mh-z19b-co2-manual(ver1_6).pdf) | [Arduino library](https://github.com/WifWaf/MH-Z19)          |
| Sensirion SCD41 | [Photoacustic](https://www.hackteria.org/wiki/Testing_and_hacking_the_SCD_41) | 55                | [SCD41](https://sensirion.com/media/documents/C4B87CE6/61652F80/Sensirion_CO2_Sensors_SCD4x_Datasheet.pdf) | [Arduino example](https://github.com/Sensirion/arduino-snippets) |

All sensors are wide range (400 to 5000 ppm or more) and its declared accuracy is around ± 40ppm. 

First two sensors were provided in the context of [Biomaker 2022](https://www.biomaker.org/challenge) and the SCD41 as part of project [UROS](https://www.hackteria.org/wiki/UROS)

## Hardware

Each sensor was connected to an Arduino UNO and to a push button used for calibration.

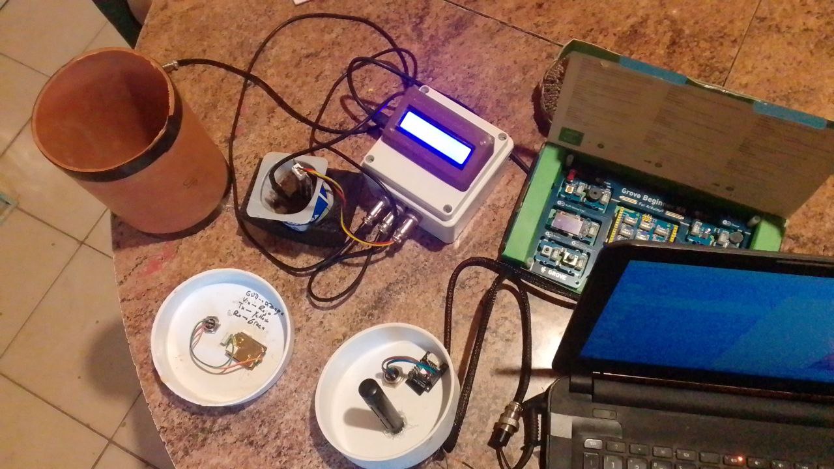
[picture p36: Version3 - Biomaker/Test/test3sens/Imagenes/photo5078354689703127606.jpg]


---TO DO--- Add schematics

## Firmware 

The firmware includes the same features for the three sensors:

- Turn off autocalibration

- Push button to allow span calibration (clean air -> aprox 400 ppm)

- Takes a measurement and sends data via serial port to the software every 30 seconds

  | [MH-Z16](https://gitlab.com/nanocastro/camara-respiracion-suelo/-/blob/master/Versionn%203%20-%20Biomaker/Firmware/CO2_MHZ16/CO2_MHZ16.ino) | [MH-Z19](https://gitlab.com/nanocastro/camara-respiracion-suelo/-/tree/master/Version2-Mza/Firmware/CO2_serial_py) | [SCD41](https://gitlab.com/nanocastro/camara-respiracion-suelo/-/blob/master/Versionn%203%20-%20Biomaker/Firmware/CO2_SDC41_calib/CO2_SDC41_calib.ino) |
  | ------------------------------------------------------------ | ------------------------------------------------------------ | ------------------------------------------------------------ |

## Software

We are using a [Python application](https://gitlab.fcen.uncu.edu.ar/pcremades/co2-chamber-plot) to read and graph data received through serial port in real time.  The software saves CO2 concentration data in a .csv format with a timestamp to allow for comparisons. 

It also calculates a linear regression of a selected range and the .png figure can be saved.

## Protocol

### Setup and calibration

Before each test all sensors were exposed to free air and then calibrated. The calibration procedure lasts 20 minutes and considers the in free air the concentration of CO2 is 400 ppm.  After calibration the sensors were left in free air for another 20 minutes.   
All sensors were connected through serial port to a computer were we open a Python instance for each to run the software. Measurements were taken every 30 seconds.

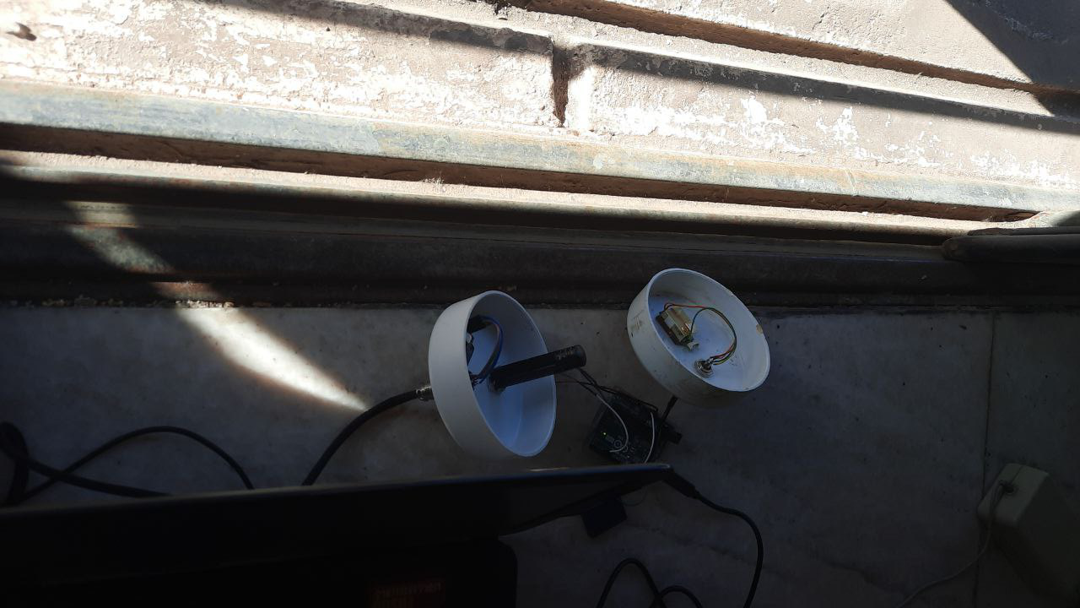
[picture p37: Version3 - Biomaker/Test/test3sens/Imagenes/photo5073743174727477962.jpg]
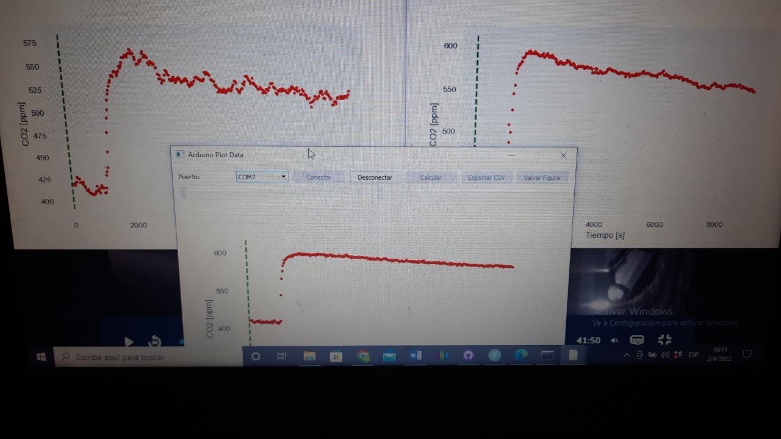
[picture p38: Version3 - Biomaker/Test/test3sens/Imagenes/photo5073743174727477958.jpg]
  

### Test chamber

The test chamber is made out of 110 mm standard sanitary pipe closed tightly by two lids were the sensors are installed. 

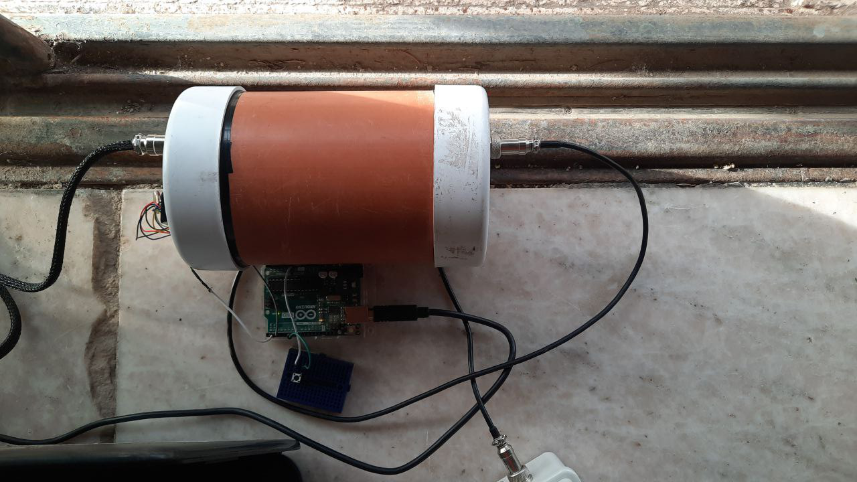
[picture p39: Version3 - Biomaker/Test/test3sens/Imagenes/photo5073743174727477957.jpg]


## Results

### Free air

After calibration the sensors were left measuring in free air for 30 minutes. 

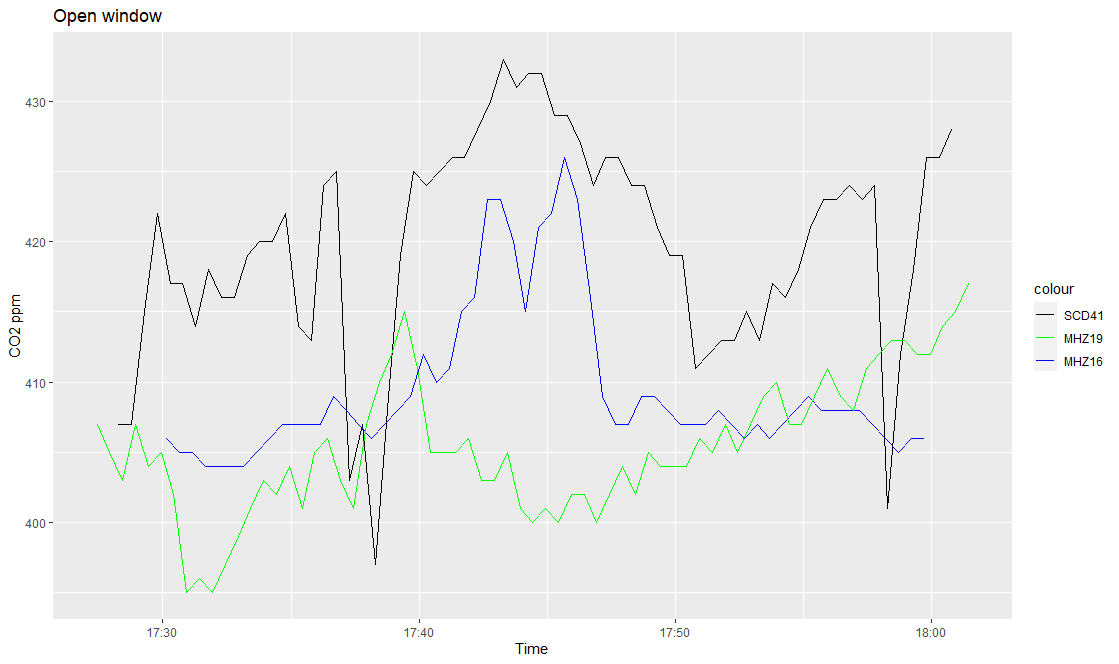
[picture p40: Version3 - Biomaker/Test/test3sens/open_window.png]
open window


| Sensor | Min.  | Median | Mean  | Max.  |
| ------ | ----- | ------ | ----- | ----- |
| MH-Z19 | 404.0 | 407.0  | 409.5 | 426.0 |
| MH-Z16 | 395.0 | 405.0  | 405.5 | 417.0 |
| SCD41  | 397.0 | 420.5  | 419.7 | 433.0 |

### Empty chamber

After calibration the sensors were exposed to free air and then the empty chamber was capped with the lids (vertical red line) . The measurement lasted for around 6 hours. 

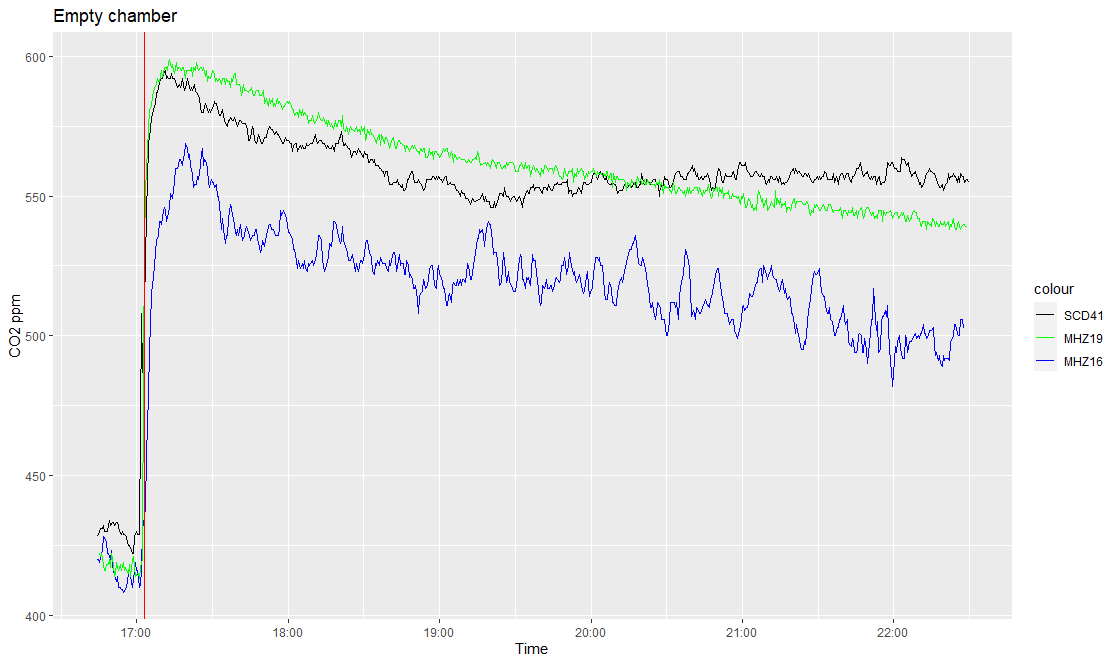
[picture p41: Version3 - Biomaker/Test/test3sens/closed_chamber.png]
closed chamber


### Rewetted soil sample

After calibration the sensors were exposed to free air and then a dry soil sample (aprox 120 gr) was rewetted with 30 ml of tap water and introduced into the chamber inside the chamber. The chamber was capped with the lids (vertical red line)  and the measurement lasted for around 6 hours. 

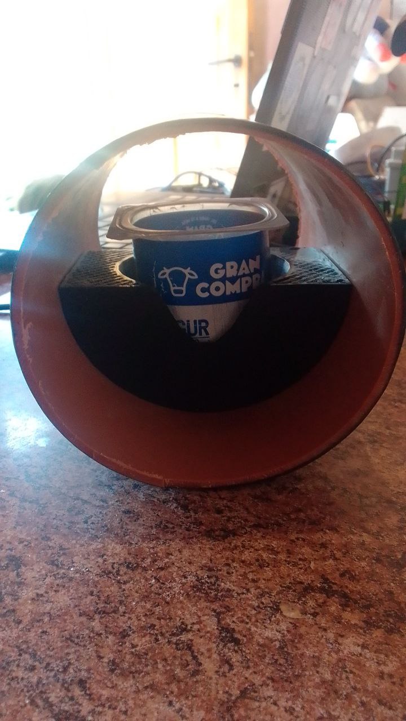
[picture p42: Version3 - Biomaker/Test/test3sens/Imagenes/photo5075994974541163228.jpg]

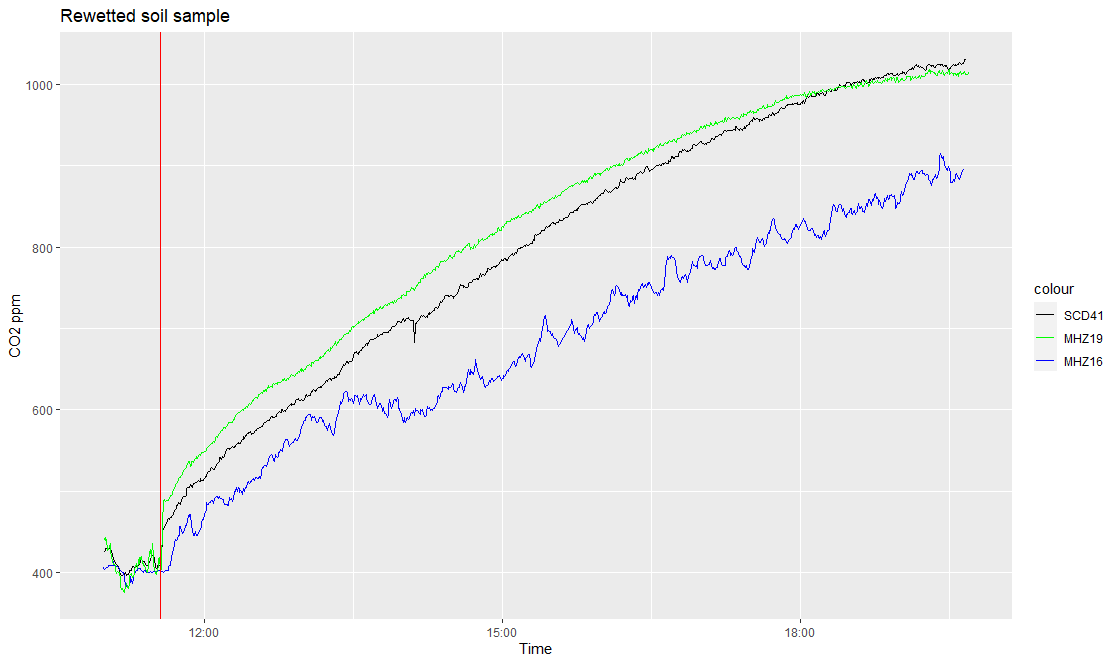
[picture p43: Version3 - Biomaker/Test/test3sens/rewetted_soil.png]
rewetted soil


## Some fast observations

### Trend
Further analysis is needed to understand better the response of different sensors but at first glance all of them follow similar paterns inside the camber. SCD41 seems like the most stable sensor and has a very similar behavior to the MH-Z19. 
The starting slope (after the clousure bump) is very similar for all three sensors. This is an important fact for short field measurements.

### Closing bump
We need to improve the how to close the chamber and to avoid a jump in concentrations. We think this is due to a great amount of air trapped in a smaller volume, giving a higher concentration. 
In field measurements this CO2 puff, were the concentration suddenly rise at closing time, is called the [dead band](https://www.youtube.com/watch?v=1EkkB8JaIzQ&ab_channel=MethodsinSoilOrganicMatterandBiogeochemistry) and is not part of the valid data.
We did some further analysis of this in our chambers (red vertical line is for closing, yellow vertical line for opening).    
First we did a normal open an closing to check the puff and then we loose a little bit the lids and the puff dimished considerably.  
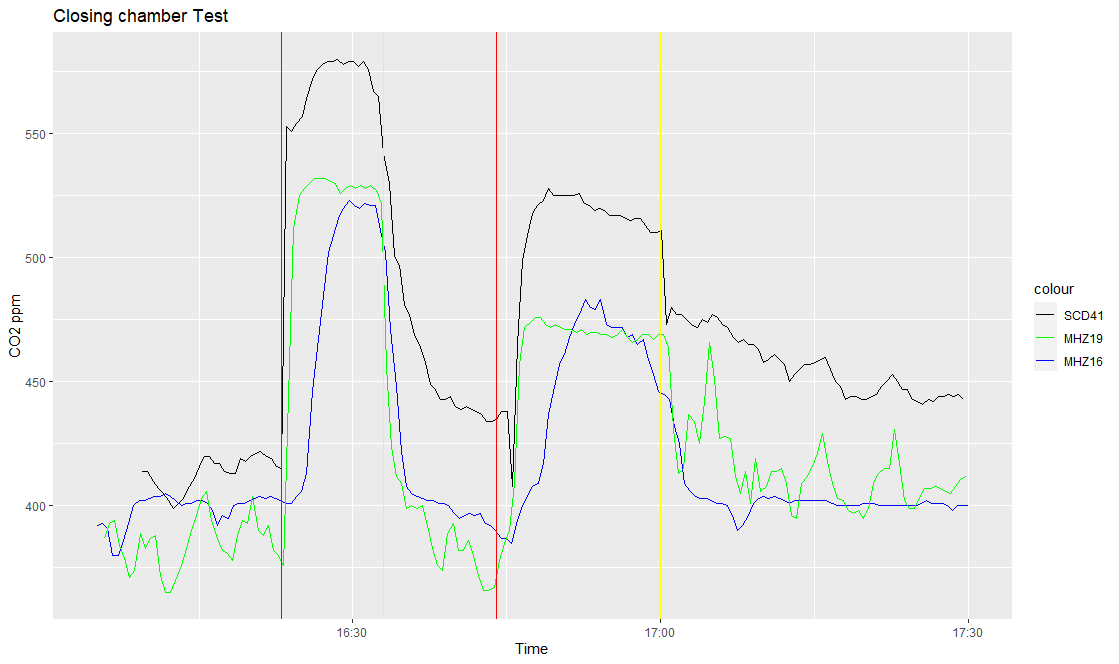
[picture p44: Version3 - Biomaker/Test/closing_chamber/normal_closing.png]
closing
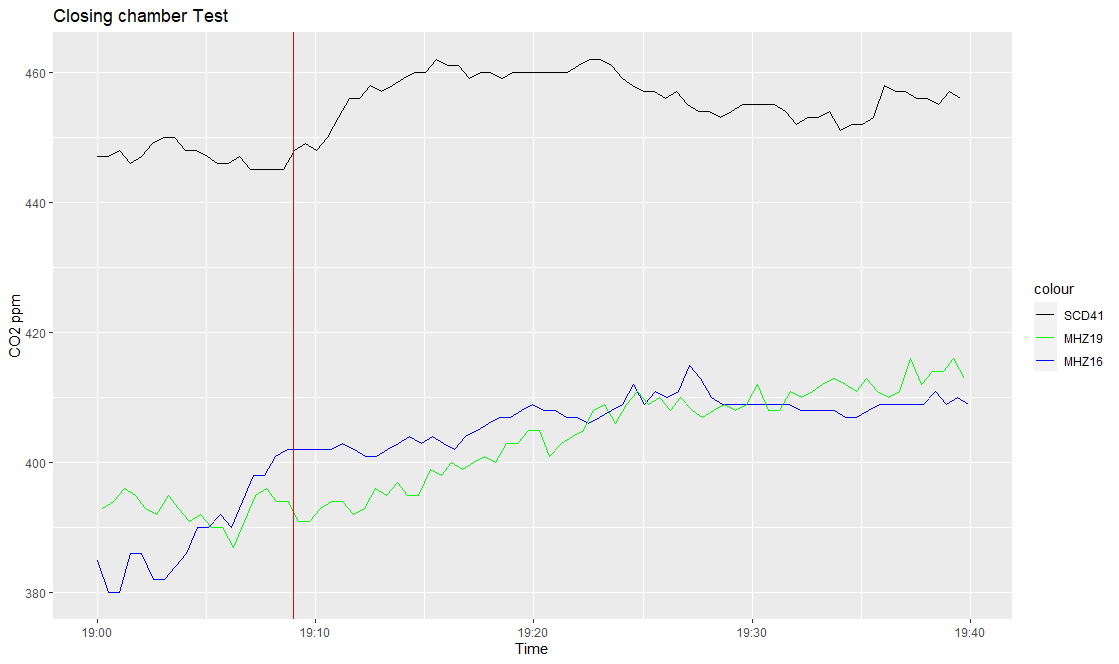
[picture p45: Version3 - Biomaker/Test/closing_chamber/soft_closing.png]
soft closing
   
We will install a BMP280 sensor inside the chamber to study better changes in pressure.
One possible solution to the closing puff is to add a small vent that can serve at compensate the pressure when closing.

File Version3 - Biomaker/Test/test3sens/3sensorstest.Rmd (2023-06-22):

---
title: "Task name: Short title"
output:
  html_document:
    df_print: paged
    toc: yes
    toc_float:
      collapsed: false
    toc_depth: 4
    number_sections: false
    smooth_scroll: false
    code_folding: hide
  pdf_document:
    latex_engine: xelatex
    toc: true
    toc_depth: 4
    number_sections: true
editor_options:
  chunk_output_type: inline
author: NM
date: "`r format(Sys.time(), '%d %B, %Y')`"
urlcolor: blue
knit: (function(inputFile, encoding) {
  rmarkdown::render(inputFile, encoding = encoding, output_dir = "output/renders") })
---

<!-- Templates are located within the inst/rmarkdown/templates directory of a package. -->

```{r setup, message=F}
knitr::opts_chunk$set(message = F)
knitr::opts_knit$set(root.dir = here::here())
library(lubridate)
library(tidyverse)
library(zoo)
```

```{r}
## Closed chamber test

mhz19<-read_csv("MH-Z19_closed chamber_1.csv")
mhz16<-read_csv("MH-Z16_closed chamber_1.csv")
scd41<-read_csv("SDC41_closed chamber_1.csv")
summary(mhz19)
summary(mhz16)
summary(scd41)
```

```{r}
ggplot() +               
  geom_line(aes(scd41$TimeStamp,scd41$Medición, color = "black") ) +  
  geom_line(aes(mhz19$TimeStamp,mhz19$Medición, color = "green")) +
  geom_line(aes(mhz16$TimeStamp,mhz16$Medición, color = "blue")) +
  geom_vline(xintercept = as.POSIXct("2022-04-02 17:00")) + 
  labs(x = "Time", y = "CO2 ppm") +
  scale_color_manual(labels = c('SCD41', 'MHZ19', 'MHZ16'),
                     values = c('black', 'green', 'blue')) +
  ggtitle("Efecto de colocar la tapa (sin suelo)")
```

```{r}
datos <- bind_rows(
  mhz19=mhz19,
  mhz16=mhz16,
  scd41=scd41,
  .id = "sensor"
)

datos %>% 
  filter(TimeStamp >= as.POSIXct("2022-04-02 17:00", tz = "UTC")) %>% 
  ggplot() +               
  geom_line(aes(x=TimeStamp, y=Medición, color = sensor)) +
  geom_vline(xintercept = as.POSIXct("2022-04-02 17:00")) + 
  labs(x = "Time", y = "CO2 ppm") +
  scale_color_manual(values = c('black', 'green', 'blue')) +
  ggtitle("Efecto de colocar la tapa (sin suelo)")
```

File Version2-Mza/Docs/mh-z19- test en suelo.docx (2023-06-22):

///////// Camara de respiración /////////

Sketch

Sensor MH-Z19 (trucho)

Codigo sensor

https://tecnologias.libres.cc/fcastro/camara-respiracion-suelo/tree/master/software/MzaTest

Se usan 2 librerías distintas para obtener los datos.

https://github.com/piot-jp-Team/mhz19_uart. Misma que Jorge Aliaga usa para su medidor de co2 ambiental

https://github.com/WifWaf/MH-Z19 mide por debajo de 400ppm

Codigo visualización y regresión

https://tecnologias.libres.cc/fcastro/camara-respiracion-suelo/blob/master/software/GUI/ArduinoPlot.py

Links

https://forum.hackteria.org/t/soil-respiration-co2-chamber-measurements/349/24

Cómo reconocer sensor original Winsen?

MH-Z19 hay uno original y unos truchos… nos tenemos los segundos

https://revspace.nl/MH-Z19B#Fake_MH-Z19B_.28black_PCB.29

Teoría respiracion de suelos

https://digitalcommons.unl.edu/cgi/viewcontent.cgi?article=2384&context=usdaarsfacpub

Primeros tests

Aire


Huerta. Húmedo. Sombra


Huerta. Seco.Sol


Tierra preparada. Bolsa. Sombra


15/4/2021

Cambio de firmware

Aire


Huerta. Sombra. Húmedo


Aire


Tierra preparada


Repeticion


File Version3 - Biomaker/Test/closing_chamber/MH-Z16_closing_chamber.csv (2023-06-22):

TimeStamp | Tiempo | Medición
2022-04-18 16:05:45 | 30.009 | 387.0
2022-04-18 16:06:15 | 60.018 | 393.0
2022-04-18 16:06:45 | 90.028 | 394.0
2022-04-18 16:07:15 | 120.037 | 384.0
2022-04-18 16:07:45 | 150.046 | 379.0
2022-04-18 16:08:15 | 180.056 | 371.0
2022-04-18 16:08:45 | 210.065 | 374.0
2022-04-18 16:09:15 | 240.074 | 389.0
2022-04-18 16:09:45 | 270.084 | 383.0
2022-04-18 16:10:15 | 300.093 | 387.0
2022-04-18 16:10:45 | 330.102 | 388.0
2022-04-18 16:11:15 | 360.112 | 372.0
2022-04-18 16:11:45 | 390.121 | 365.0
2022-04-18 16:12:15 | 420.13 | 365.0
2022-04-18 16:12:45 | 450.14 | 370.0
2022-04-18 16:13:15 | 480.149 | 376.0
2022-04-18 16:13:45 | 510.158 | 383.0
2022-04-18 16:14:15 | 540.168 | 390.0
2022-04-18 16:14:45 | 570.177 | 396.0
2022-04-18 16:15:15 | 600.186 | 403.0
2022-04-18 16:15:45 | 630.196 | 406.0
2022-04-18 16:16:15 | 660.205 | 394.0
2022-04-18 16:16:45 | 690.214 | 387.0
2022-04-18 16:17:15 | 720.223 | 382.0
2022-04-18 16:17:45 | 750.232 | 381.0
2022-04-18 16:18:15 | 780.241 | 378.0
2022-04-18 16:18:45 | 810.25 | 388.0
2022-04-18 16:19:15 | 840.259 | 394.0
2022-04-18 16:19:45 | 870.268 | 393.0
2022-04-18 16:20:15 | 900.277 | 404.0
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

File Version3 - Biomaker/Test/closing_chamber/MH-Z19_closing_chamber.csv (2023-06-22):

TimeStamp | Tiempo | Medición
2022-04-18 16:05:04 | 0.0 | 392.0
2022-04-18 16:05:35 | 61.877 | 393.0
2022-04-18 16:06:05 | 92.581 | 391.0
2022-04-18 16:06:36 | 123.286 | 380.0
2022-04-18 16:07:07 | 153.991 | 380.0
2022-04-18 16:07:37 | 184.696 | 386.0
2022-04-18 16:08:08 | 215.402 | 393.0
2022-04-18 16:08:39 | 246.107 | 400.0
2022-04-18 16:09:09 | 276.811 | 402.0
2022-04-18 16:09:40 | 307.516 | 402.0
2022-04-18 16:10:11 | 338.222 | 403.0
2022-04-18 16:10:41 | 368.927 | 404.0
2022-04-18 16:11:12 | 399.632 | 404.0
2022-04-18 16:11:43 | 430.338 | 405.0
2022-04-18 16:12:14 | 461.043 | 404.0
2022-04-18 16:12:44 | 491.749 | 402.0
2022-04-18 16:13:15 | 522.455 | 400.0
2022-04-18 16:13:45 | 553.16 | 401.0
2022-04-18 16:14:16 | 583.866 | 401.0
2022-04-18 16:14:47 | 614.572 | 402.0
2022-04-18 16:15:18 | 645.276 | 402.0
2022-04-18 16:15:48 | 675.982 | 401.0
2022-04-18 16:16:19 | 706.688 | 398.0
2022-04-18 16:16:50 | 737.393 | 392.0
2022-04-18 16:17:20 | 768.099 | 396.0
2022-04-18 16:17:51 | 798.804 | 395.0
2022-04-18 16:18:22 | 829.509 | 400.0
2022-04-18 16:18:52 | 860.215 | 401.0
2022-04-18 16:19:23 | 890.92 | 401.0
2022-04-18 16:19:54 | 921.625 | 402.0
2022-04-18 16:20:24 | 952.331 | 403.0
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

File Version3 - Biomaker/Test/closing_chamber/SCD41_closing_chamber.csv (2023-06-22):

TimeStamp | Tiempo | Medición
2022-04-18 16:09:31 | 0.0 | 414.0
2022-04-18 16:10:01 | 30.002 | 414.0
2022-04-18 16:10:31 | 60.004 | 410.0
2022-04-18 16:11:01 | 90.006 | 407.0
2022-04-18 16:11:31 | 120.008 | 405.0
2022-04-18 16:12:01 | 150.01 | 402.0
2022-04-18 16:12:31 | 180.013 | 399.0
2022-04-18 16:13:01 | 210.015 | 401.0
2022-04-18 16:13:31 | 240.017 | 403.0
2022-04-18 16:14:02 | 270.019 | 408.0
2022-04-18 16:14:31 | 300.021 | 411.0
2022-04-18 16:15:02 | 330.023 | 416.0
2022-04-18 16:15:32 | 360.025 | 420.0
2022-04-18 16:16:01 | 390.027 | 420.0
2022-04-18 16:16:31 | 420.029 | 417.0
2022-04-18 16:17:01 | 450.031 | 417.0
2022-04-18 16:17:31 | 480.033 | 414.0
2022-04-18 16:18:01 | 510.035 | 413.0
2022-04-18 16:18:32 | 540.037 | 413.0
2022-04-18 16:19:01 | 570.039 | 419.0
2022-04-18 16:19:31 | 600.041 | 418.0
2022-04-18 16:20:01 | 630.043 | 420.0
2022-04-18 16:20:32 | 660.045 | 421.0
2022-04-18 16:21:01 | 690.048 | 422.0
2022-04-18 16:21:32 | 720.05 | 420.0
2022-04-18 16:22:02 | 750.052 | 419.0
2022-04-18 16:22:32 | 780.054 | 416.0
2022-04-18 16:23:02 | 810.056 | 415.0
2022-04-18 16:23:32 | 840.058 | 553.0
2022-04-18 16:24:02 | 870.061 | 551.0
2022-04-18 16:24:31 | 900.063 | 554.0
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

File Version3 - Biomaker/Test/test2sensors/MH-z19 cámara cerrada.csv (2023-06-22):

TimeStamp | Tiempo | Medición
2022-03-03 11:09:14 | 91.305 | 406.0
2022-03-03 11:09:44 | 121.37 | 460.0
2022-03-03 11:10:14 | 151.436 | 488.0
2022-03-03 11:10:44 | 181.502 | 503.0
2022-03-03 11:11:14 | 211.569 | 522.0
2022-03-03 11:11:44 | 241.637 | 527.0
2022-03-03 11:12:14 | 271.703 | 527.0
2022-03-03 11:12:45 | 301.77 | 531.0
2022-03-03 11:13:14 | 331.838 | 535.0
2022-03-03 11:13:45 | 361.904 | 539.0
2022-03-03 11:14:15 | 391.971 | 543.0
2022-03-03 11:14:45 | 422.037 | 540.0
2022-03-03 11:15:15 | 452.104 | 535.0
2022-03-03 11:15:45 | 482.169 | 530.0
2022-03-03 11:16:15 | 512.237 | 527.0
2022-03-03 11:16:45 | 542.303 | 527.0
2022-03-03 11:17:15 | 572.37 | 526.0
2022-03-03 11:17:45 | 602.437 | 535.0
2022-03-03 11:18:15 | 632.503 | 527.0
2022-03-03 11:18:45 | 662.568 | 522.0
2022-03-03 11:19:15 | 692.635 | 521.0
2022-03-03 11:19:45 | 722.701 | 527.0
2022-03-03 11:20:15 | 752.769 | 533.0
2022-03-03 11:20:45 | 782.834 | 533.0
2022-03-03 11:21:15 | 812.901 | 533.0
2022-03-03 11:21:46 | 842.969 | 532.0
2022-03-03 11:22:16 | 873.036 | 532.0
2022-03-03 11:22:45 | 903.104 | 535.0
2022-03-03 11:23:16 | 933.172 | 538.0
2022-03-03 11:23:46 | 963.237 | 538.0
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

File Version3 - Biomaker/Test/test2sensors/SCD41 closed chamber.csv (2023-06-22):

TimeStamp | Tiempo | Medición
2022-03-03 11:09:23 | 0.0 | 506.0
2022-03-03 11:09:53 | 30.002 | 508.0
2022-03-03 11:10:22 | 60.004 | 509.0
2022-03-03 11:10:52 | 90.006 | 509.0
2022-03-03 11:11:22 | 120.008 | 511.0
2022-03-03 11:11:53 | 150.01 | 513.0
2022-03-03 11:12:23 | 180.013 | 517.0
2022-03-03 11:12:53 | 210.015 | 517.0
2022-03-03 11:13:23 | 240.017 | 520.0
2022-03-03 11:13:53 | 270.019 | 519.0
2022-03-03 11:14:22 | 300.021 | 520.0
2022-03-03 11:14:52 | 330.023 | 520.0
2022-03-03 11:15:23 | 360.025 | 521.0
2022-03-03 11:15:53 | 390.027 | 521.0
2022-03-03 11:16:22 | 420.029 | 521.0
2022-03-03 11:16:53 | 450.031 | 522.0
2022-03-03 11:17:23 | 480.033 | 525.0
2022-03-03 11:17:53 | 510.035 | 526.0
2022-03-03 11:18:23 | 540.037 | 524.0
2022-03-03 11:18:53 | 570.039 | 529.0
2022-03-03 11:19:22 | 600.041 | 529.0
2022-03-03 11:19:53 | 630.043 | 529.0
2022-03-03 11:20:23 | 660.045 | 530.0
2022-03-03 11:20:53 | 690.048 | 529.0
2022-03-03 11:21:23 | 720.05 | 530.0
2022-03-03 11:21:53 | 750.052 | 533.0
2022-03-03 11:22:22 | 780.054 | 533.0
2022-03-03 11:22:53 | 810.056 | 534.0
2022-03-03 11:23:23 | 840.058 | 535.0
2022-03-03 11:23:53 | 870.061 | 538.0
2022-03-03 11:24:23 | 900.063 | 536.0
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

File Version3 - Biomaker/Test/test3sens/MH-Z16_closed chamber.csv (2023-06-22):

TimeStamp | Tiempo | Medición
2022-03-29 17:10:24 | 30.009 | 539.0
2022-03-29 17:10:54 | 60.018 | 543.0
2022-03-29 17:11:24 | 90.028 | 545.0
2022-03-29 17:11:53 | 120.037 | 543.0
2022-03-29 17:12:23 | 150.046 | 544.0
2022-03-29 17:12:53 | 180.056 | 546.0
2022-03-29 17:13:23 | 210.065 | 546.0
2022-03-29 17:13:53 | 240.074 | 546.0
2022-03-29 17:14:24 | 270.084 | 544.0
2022-03-29 17:14:53 | 300.093 | 544.0
2022-03-29 17:15:24 | 330.102 | 543.0
2022-03-29 17:15:53 | 360.112 | 543.0
2022-03-29 17:16:24 | 390.121 | 543.0
2022-03-29 17:16:54 | 420.13 | 547.0
2022-03-29 17:17:24 | 450.14 | 547.0
2022-03-29 17:17:54 | 480.149 | 548.0
2022-03-29 17:18:24 | 510.158 | 547.0
2022-03-29 17:18:54 | 540.168 | 546.0
2022-03-29 17:19:24 | 570.177 | 545.0
2022-03-29 17:19:53 | 600.186 | 546.0
2022-03-29 17:20:24 | 630.196 | 547.0
2022-03-29 17:20:54 | 660.205 | 545.0
2022-03-29 17:21:24 | 690.214 | 545.0
2022-03-29 17:21:54 | 720.223 | 544.0
2022-03-29 17:22:23 | 750.232 | 542.0
2022-03-29 17:22:54 | 780.241 | 544.0
2022-03-29 17:23:23 | 810.25 | 543.0
2022-03-29 17:23:54 | 840.259 | 543.0
2022-03-29 17:24:24 | 870.268 | 545.0
2022-03-29 17:24:53 | 900.277 | 541.0
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

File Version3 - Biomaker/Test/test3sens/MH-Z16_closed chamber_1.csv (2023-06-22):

TimeStamp | Tiempo | Medición
2022-04-02 16:45:03 | 30.009 | 422.0
2022-04-02 16:45:33 | 60.018 | 421.0
2022-04-02 16:46:03 | 90.028 | 422.0
2022-04-02 16:46:33 | 120.037 | 418.0
2022-04-02 16:47:03 | 150.046 | 416.0
2022-04-02 16:47:33 | 180.056 | 416.0
2022-04-02 16:48:03 | 210.065 | 418.0
2022-04-02 16:48:33 | 240.074 | 418.0
2022-04-02 16:49:03 | 270.084 | 420.0
2022-04-02 16:49:33 | 300.093 | 417.0
2022-04-02 16:50:03 | 330.102 | 422.0
2022-04-02 16:50:33 | 360.112 | 418.0
2022-04-02 16:51:03 | 390.121 | 414.0
2022-04-02 16:51:33 | 420.13 | 415.0
2022-04-02 16:52:03 | 450.14 | 419.0
2022-04-02 16:52:33 | 480.149 | 416.0
2022-04-02 16:53:03 | 510.158 | 417.0
2022-04-02 16:53:33 | 540.168 | 418.0
2022-04-02 16:54:03 | 570.177 | 416.0
2022-04-02 16:54:33 | 600.186 | 419.0
2022-04-02 16:55:03 | 630.196 | 416.0
2022-04-02 16:55:33 | 660.205 | 417.0
2022-04-02 16:56:03 | 690.214 | 416.0
2022-04-02 16:56:33 | 720.223 | 415.0
2022-04-02 16:57:03 | 750.232 | 418.0
2022-04-02 16:57:33 | 780.241 | 414.0
2022-04-02 16:58:03 | 810.25 | 420.0
2022-04-02 16:58:33 | 840.259 | 421.0
2022-04-02 16:59:03 | 870.268 | 417.0
2022-04-02 16:59:33 | 900.277 | 414.0
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

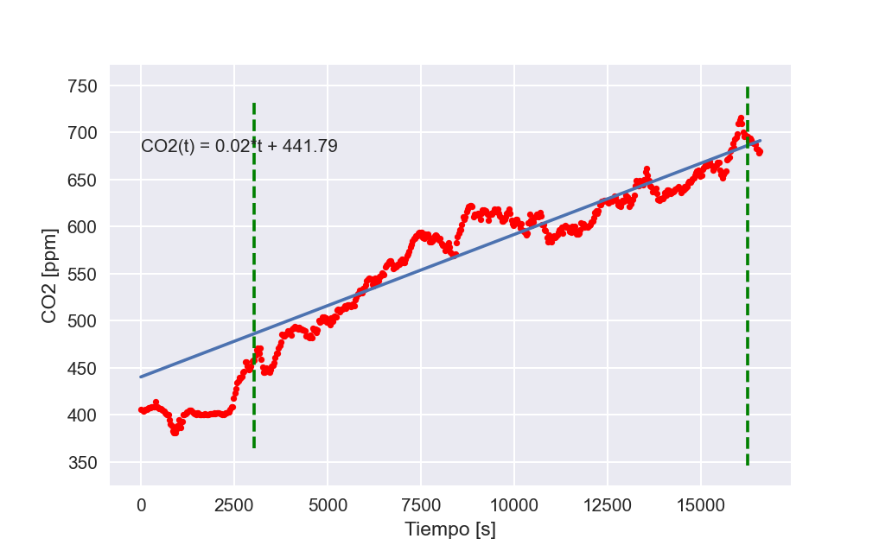
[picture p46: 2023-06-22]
Version3 - Biomaker/Test/test3sens/MH-Z19_rewetted soil.png

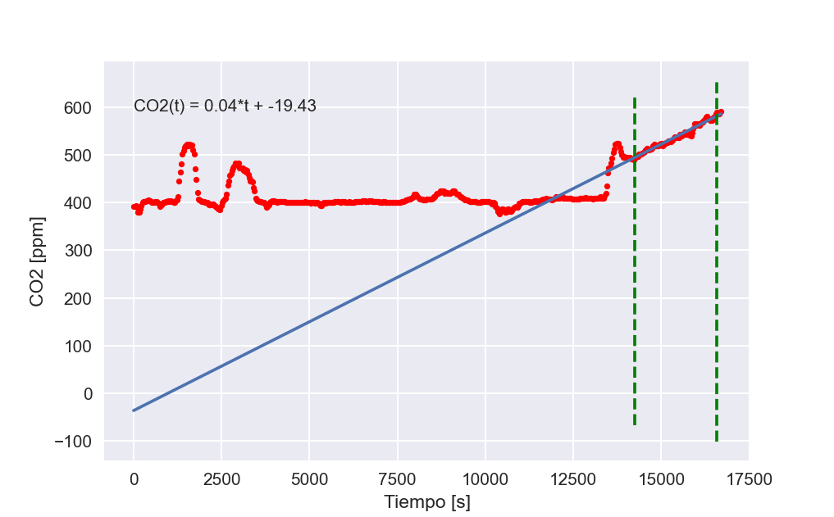
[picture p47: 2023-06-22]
Version3 - Biomaker/Test/closing_chamber/MH-Z19_closing_chamber.png

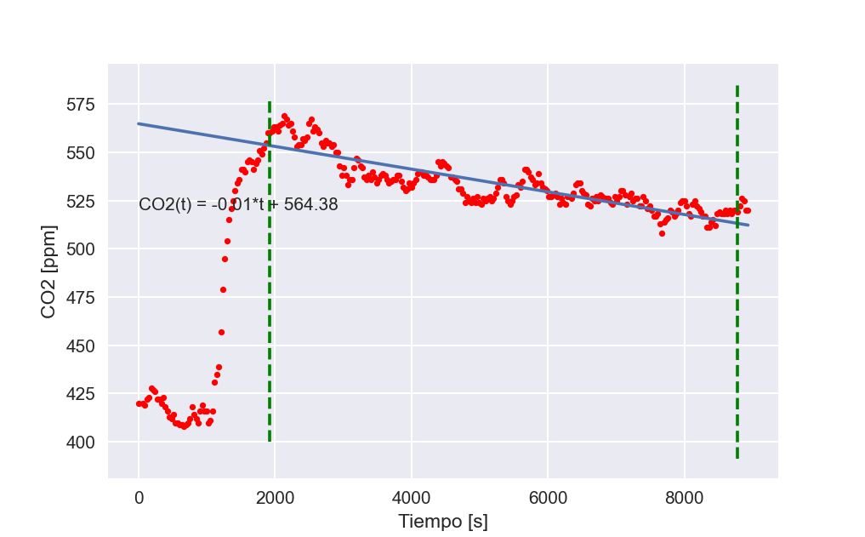
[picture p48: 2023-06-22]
Version3 - Biomaker/Test/test3sens/MH-Z19_closed chamber_1.png

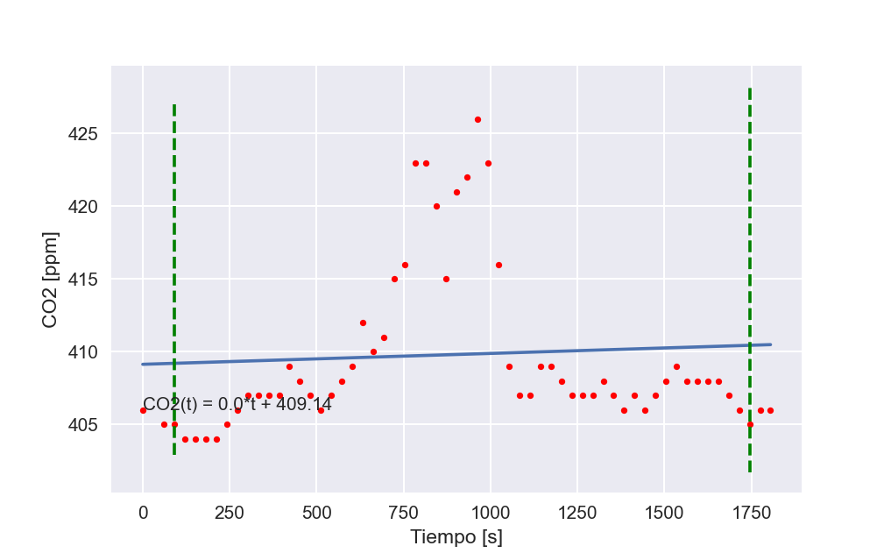
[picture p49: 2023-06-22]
Version3 - Biomaker/Test/test3sens/MH-Z19_open window.png

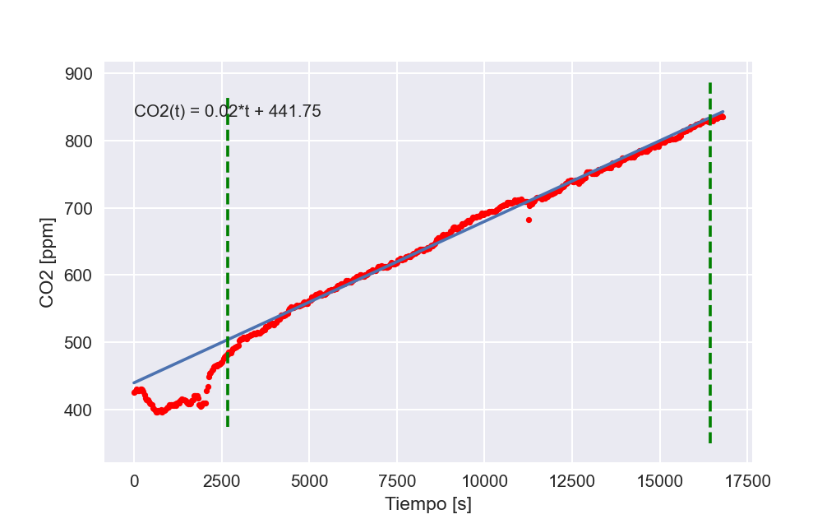
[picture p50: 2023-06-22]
Version3 - Biomaker/Test/test3sens/SDC41_rewetted soil.png

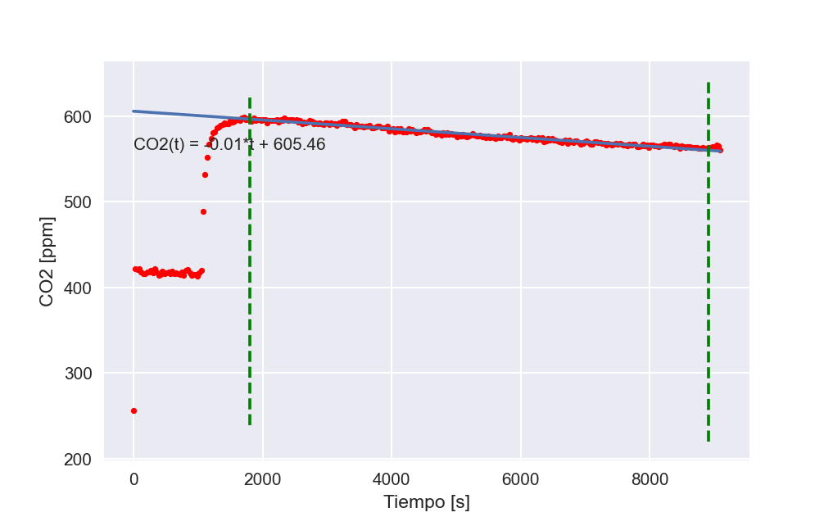
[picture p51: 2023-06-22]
Version3 - Biomaker/Test/test3sens/MH-Z16_closed chamber_1.png

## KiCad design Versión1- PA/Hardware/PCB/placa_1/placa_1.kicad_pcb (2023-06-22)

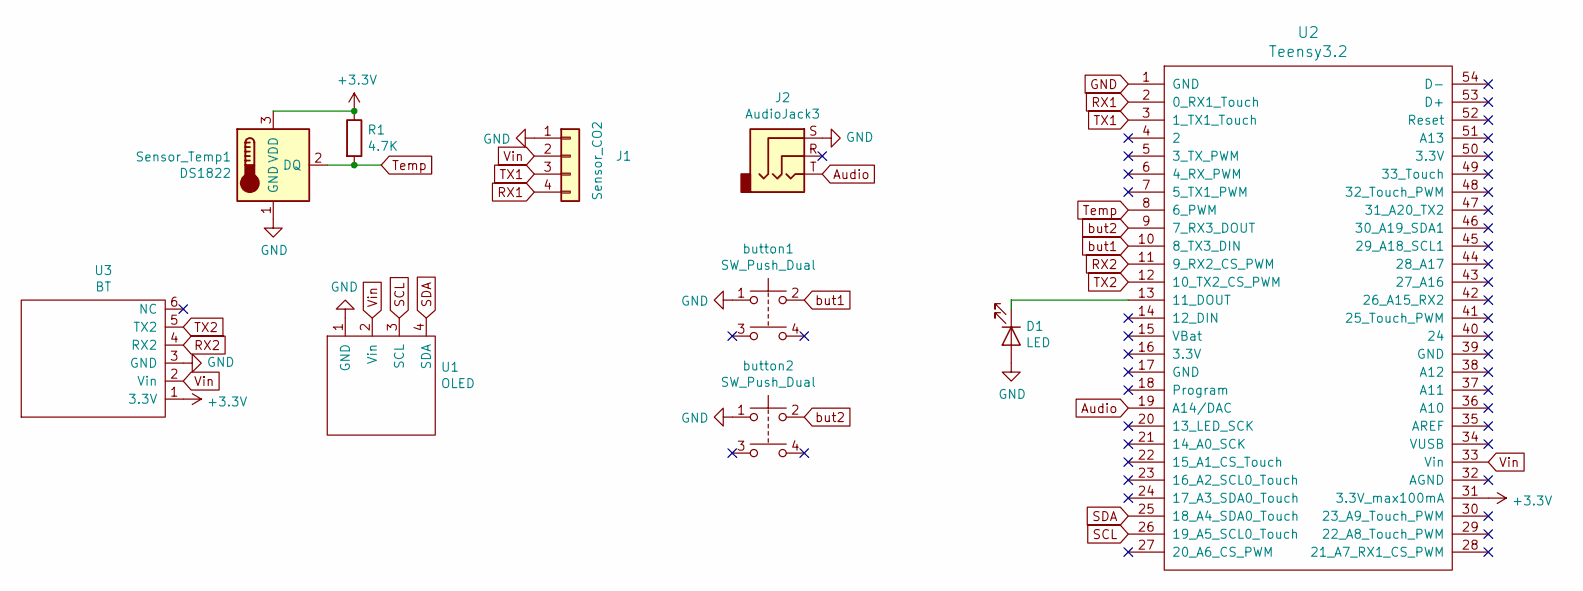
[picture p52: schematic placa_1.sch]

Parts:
D1: LED; LED_D3.0mm_IRBlack
J1: Sensor_CO2; PinHeader_1x04_P2.54mm_Vertical
J2: AudioJack3; AudioJack
R1: 4.7K; R_Axial_DIN0207_L6.3mm_D2.5mm_P7.62mm_Horizontal
Sensor_Temp1: DS1822; PinHeader_1x03_P2.54mm_Vertical
U1: OLED; PinHeader_1x04_P2.54mm_Vertical
U2: Teensy3.2; Teensy30_31_32_LC
U3: BT; PinHeader_1x06_P2.54mm_Vertical
button1, button2: SW_Push_Dual; SW_PUSH_6mm

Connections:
+3V3: R1.1, Sensor_Temp1.3 (VDD), U2.31 (3.3V_max100mA), U3.1 (3.3V)
Audio: J2.T, U2.19 (A14/DAC)
GND: D1.2 (A), J1.1, J2.S, Sensor_Temp1.1 (GND), U1.1 (GND), U2.1 (GND), U3.3 (GND), button1.1, button2.1
unnamed: D1.1 (K), U2.13 (11_DOUT)
RX1: J1.4, U2.2 (0_RX1_Touch)
RX2: U2.11 (9_RX2_CS_PWM), U3.4 (RX2)
SCL: U1.3 (SCL), U2.26 (19_A5_SCL0_Touch)
SDA: U1.4 (SDA), U2.25 (18_A4_SDA0_Touch)
TX1: J1.3, U2.3 (1_TX1_Touch)
TX2: U2.12 (10_TX2_CS_PWM), U3.5 (TX2)
Temp: R1.2, Sensor_Temp1.2 (DQ), U2.8 (6_PWM)
Vin: J1.2, U1.2 (Vin), U2.33 (Vin), U3.2 (Vin)
but1: U2.10 (8_TX3_DIN), button1.2
but2: U2.9 (7_RX3_DOUT), button2.2

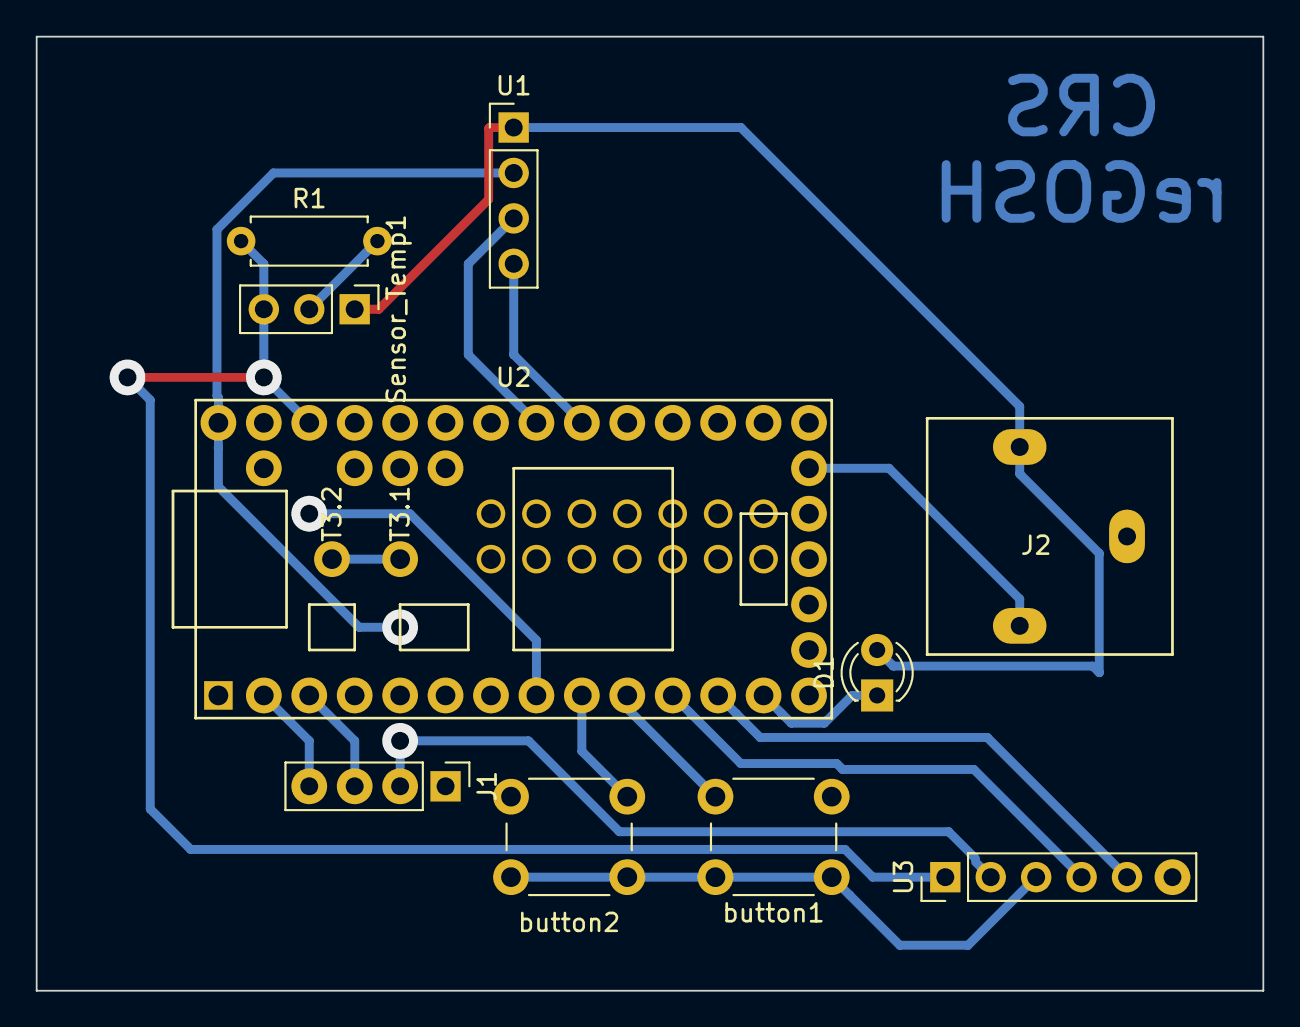
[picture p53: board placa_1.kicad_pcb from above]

Board: 2 copper layers, 68.6 x 53.3 mm, 10 parts (0 on the bottom side), 14 nets.

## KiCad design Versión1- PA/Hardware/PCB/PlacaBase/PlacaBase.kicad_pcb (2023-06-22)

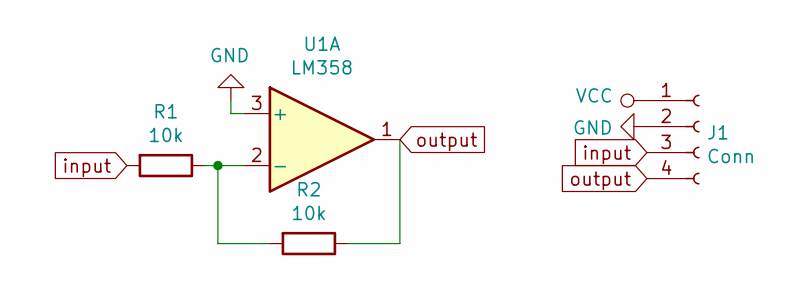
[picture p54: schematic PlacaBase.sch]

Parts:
J1: Conn; PinHeader_1x04_P1.00mm_Vertical
R1, R2: 10k; R_Axial_DIN0204_L3.6mm_D1.6mm_P5.08mm_Horizontal
U1: LM358; DIP-8_W7.62mm_Socket

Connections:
GND: J1.2, U1.3 (+)
unnamed: R1.1, R2.2, U1.2 (-)
VCC: J1.1
input: J1.3, R1.2
output: J1.4, R2.1, U1.1

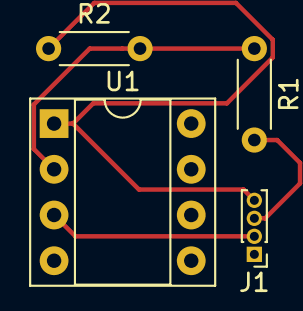
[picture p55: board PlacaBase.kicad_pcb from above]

Board: 2 copper layers, 4 parts (0 on the bottom side), 4 nets.

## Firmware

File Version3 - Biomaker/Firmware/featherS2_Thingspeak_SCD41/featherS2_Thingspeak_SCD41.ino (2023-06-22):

 /*
 * dusjagr edited some stuffs...
 * Adding display
 * Adding timer
 * Adding BMP280 pressure sensor
 * Adding Neo-Pixel on pin 18
 * Adding Dallas Temperature sensor for external use of soil temperature probe
 * different version of OneWireNG had to be used to compile correctly on ESP32 S2
 * Not finished: proper calibration routine
 * 
 */

#define BMP_IS_ATTACHED
#define DS18x20_IS_ATTACHED
#define USE_THINGSPEAK

#include <Arduino.h>
#include <SensirionI2CScd4x.h>
#include <Wire.h>
#include <Adafruit_NeoPixel.h>

const int LEDonBoard = 13;       // the number of the LED pin
const int LEDexternal = 33;      // the number of the LED pin
const int buttonPin = 38;        // the number of the pushbutton pin
const int cal_pin = 0;           // entrada pulsador calibración
int ledState = LOW;              // ledState used to set the LED
int buttonState = HIGH;          // the current reading from the input pin
int lastButtonState = HIGH;      // the previous reading from the input pin
int screenState = 0;             // different views on the OLED screen

unsigned long lastDebounceTime = 0;  // the last time the output pin was toggled
unsigned long debounceDelay = 50;    // the debounce time; increase if the output flickers

const int neoPixelPin = 7;          // NeoPixel for UROS board
const int neoPixelcount = 1;         // How many NeoPixels are attached?
int neoBrightness = 25;

  float BMP280temp = -1;
  float BMP280preshPa = -1;
  float soilTemperatureC = -1;
  uint32_t BMP280pres = -1;
  float BMP280alti = -1;

// Declare our NeoPixel object:
Adafruit_NeoPixel neopixel(neoPixelcount, neoPixelPin, NEO_GRB + NEO_KHZ800);

// SCD41 calibration settings *******
// ==================================

uint16_t alt = 15;
uint32_t pressureCalibration;
float tempOffset = 2.0;
bool ascSetting = false; // Turn automatic self calibration off

// DS18x20 stuffs *******************
// ==================================

#ifdef DS18x20_IS_ATTACHED
  #include <OneWireNg_Config.h>
  #include <OneWireNg_BitBang.h>
  #include <OneWireNg_CurrentPlatform.h>
  #include <OneWireNg.h>
  #include <DallasTemperature.h>

  // GPIO where the DS18B20 is connected to
  const int oneWireBus = 10;  
  unsigned long DS18x20DataTimer = 0;   
  OneWire oneWire(oneWireBus);
  DallasTemperature DS18x20sensors(&oneWire);
  // arrays to hold device address
  DeviceAddress soilThermometer;

  //float soilTemperatureC;

  // function to print a device address
void printAddress(DeviceAddress deviceAddress)
{
  for (uint8_t i = 0; i < 8; i++)
  {
    if (deviceAddress[i] < 16) Serial.print("0");
    Serial.print(deviceAddress[i], HEX);
  }
}
#endif

// BMP280 stuffs ********************
// ==================================

#ifdef BMP_IS_ATTACHED
  #include <Adafruit_BMP280.h>
  Adafruit_BMP280 bmp; // I2C

  #define SEA_LEVEL_PRESSURE    1010.0f   // sea level pressure 1013.25

  //float BMP280temp;
  //uint32_t BMP280pres;
  //float BMP280preshPa;
  //float BMP280alti;
  unsigned long BMP280DataTimer = 0;
#endif

// OLED stuffs **********************
// ==================================

#include <Adafruit_GFX.h>
#include <Adafruit_SSD1306.h>

#define OLED_RESET 4
#define SCREEN_ADDRESS 0x3C
#define SCREEN_WIDTH 128 // OLED display width, in pixels
#define SCREEN_HEIGHT 64 // OLED display height, in pixels
uint32_t displayLimit = 1400;
uint32_t displayFactor = displayLimit / 48;
uint32_t meas_counter = 0;
int32_t thresholdPPM = 450;

Adafruit_SSD1306 display(SCREEN_WIDTH, SCREEN_HEIGHT, &Wire, OLED_RESET);

// """"""""""""""""""""""""""""""""""

// Sensirion SCD4x stuffs ***********
// ==================================

SensirionI2CScd4x scd4x;

unsigned long getDataTimer = 0;
unsigned long TimeSec = 0;
unsigned long timeElapse = 0;//used to wait the sensor to stabilize before calibration
uint16_t error;
char errorMessage[256];
uint16_t co2;
float temperature;
float humidity;

void printUint16Hex(uint16_t value) {
    Serial.print(value < 4096 ? "0" : "");
    Serial.print(value < 256 ? "0" : "");
    Serial.print(value < 16 ? "0" : "");
    Serial.print(value, HEX);
}

void printSerialNumber(uint16_t serial0, uint16_t serial1, uint16_t serial2) {
    Serial.print("Serial: 0x");
    printUint16Hex(serial0);
    printUint16Hex(serial1);
    printUint16Hex(serial2);
    Serial.println();
}




// THINGSSPEAK ********************
// ==================================

#ifdef USE_THINGSPEAK
  #include <WiFi.h>
  #include "secrets.h"
  #include "ThingSpeak.h" // always include thingspeak header file after other header files and custom macros
  
  char ssid[] = SECRET_SSID;   // your network SSID (name) 
  char pass[] = SECRET_PASS;   // your network password
  int keyIndex = 0;            // your network key Index number (needed only for WEP)
  WiFiClient  client;
  
  unsigned long myChannelNumber = SECRET_CH_ID;
  const char * myWriteAPIKey = SECRET_WRITE_APIKEY;

void connectWifi(){
    // Connect or reconnect to WiFi
    if(WiFi.status() != WL_CONNECTED){
      OLEDtestWiFi();
      neopixel.setPixelColor(0, neopixel.Color(0, 0, 255));
      neopixel.show();
      Serial.print("Attempting to connect to SSID: ");
      Serial.println(SECRET_SSID);
      while(WiFi.status() != WL_CONNECTED){
        WiFi.begin(ssid, pass);  // Connect to WPA/WPA2 network. Change this line if using open or WEP network
        Serial.print(".");
        delay(2000);
        neopixel.setPixelColor(0, neopixel.Color(255, 0, 0));
        neopixel.show();
        delay(2000);
        neopixel.clear();
        neopixel.show();     
      } 
      Serial.println("\nConnected.");
      neopixel.setPixelColor(0, neopixel.Color(0, 255, 0));
      neopixel.show();
      OLEDtestSuccess();
      delay(2000);
      OLEDdrawBackground();
    }
}
  
#endif

void setup() {
    
    Serial.begin(115200);
    //while ( !Serial ) delay(100);   // wait for native usb
    delay(500);
    Serial.println("    ");
    Serial.println("=========== Booting ROŠA System ===========");
    pinMode(LEDonBoard, OUTPUT);
    digitalWrite(LEDonBoard, HIGH);
    pinMode(LEDexternal, OUTPUT);
    digitalWrite(LEDexternal, HIGH);
    pinMode(buttonPin, INPUT_PULLUP);
    pinMode(cal_pin, INPUT_PULLUP); // entrada pulsado para calibrar, seteada como pulluppara poder conectar pulsador sin poenr resistencia adicional
    
    Serial.println("    ");
    
    Serial.println("=========== Turn on NEO Pixel ==================");
    neopixel.begin();           // INITIALIZE NeoPixel strip object (REQUIRED)
    delay(100);
    neopixel.clear();
    neopixel.show();
    neopixel.setBrightness(neoBrightness); // Set BRIGHTNESS to about 1/5 (max = 255)

    //rainbow(5);             // Flowing rainbow cycle along the whole strip
    //rainbowCycle(5);
    neopixel.setPixelColor(0, neopixel.Color(255, 0, 255));
    neopixel.show();
    

    Serial.println("    ");
    Serial.println("=========== Initializing OLED Screen ===========");
    initDisplay();
    Serial.println("    ");
    delay(100);

    showLogo_hackteria();
    delay(1000);
    neopixel.clear();
    neopixel.show();
    showLogo_regosh();
    delay(1000);
    showLogo_humus_text();
    delay(1000);
    neopixel.clear();
    neopixel.show();
    display.clearDisplay();

    Serial.println("    ");
        
    Serial.println("=========== Turn on Wifi ==================");

#ifdef USE_THINGSPEAK
    //WiFi.mode(WIFI_STA);   
    ThingSpeak.begin(client);  // Initialize ThingSpeak
    Serial.println("Starting WiFi");
    
    connectWifi();
#endif

    Serial.println("    ");

    Serial.println("============ Testing DS18x20 Sensor ============");

// needs to be finished
//*****************************************
#ifndef DS18x20_IS_ATTACHED
    Serial.println("DS18x20 not in use");
    OLEDtestDS18b20();
    delay(500);
    OLEDnotinuse();
    delay(2000);
#endif

#ifdef DS18x20_IS_ATTACHED
    Serial.println("DS18x20: begin");
    OLEDtestDS18b20();
    DS18x20sensors.begin();

    Serial.print("DS18x20: Found ");
    Serial.print(DS18x20sensors.getDeviceCount(), DEC);
    Serial.println(" devices.");

    if (!DS18x20sensors.getAddress(soilThermometer, 0)) {
      Serial.println("Unable to find address for Device 0");
      delay(500);
      showError(); //ERROR
    } else {
      delay(500);
      OLEDtestSuccess();
    }

    Serial.print("DS18x20: Device 0 Address: ");
    printAddress(soilThermometer);
    Serial.println();

    // set the resolution to 9 bit (Each Dallas/Maxim device is capable of several different resolutions)
    DS18x20sensors.setResolution(soilThermometer, 12);
 
    Serial.print("DS18x20: Device 0 Resolution: ");
    Serial.print(DS18x20sensors.getResolution(soilThermometer), DEC); 
    Serial.println();
    
    DS18x20sensors.requestTemperatures(); 
    soilTemperatureC = DS18x20sensors.getTempCByIndex(0);
    Serial.println("DS18x20: read once:");
    Serial.print("Soil Temperature: ");
    Serial.print(soilTemperatureC);
    Serial.println(" ºC");
    delay(1000);

    Serial.println("==================  end test  ==================");
    Serial.println();
#endif

    Serial.println("======== Testing BMP280 Pressure Sensor ========");
    
#ifndef BMP_IS_ATTACHED
    Serial.println("BMP280 not in use");
    OLEDtestBMP280();
    delay(500);
    OLEDnotinuse();
    delay(2000);
#endif

#ifdef BMP_IS_ATTACHED
    unsigned status;
    Serial.println("BMP280: begin");
    status = bmp.begin(0x76, BMP280_CHIPID);
    //status = bmp.begin(0x77, BMP280_CHIPID);
    
    OLEDtestBMP280();
    delay(500);
    if (!status) {
      Serial.println(F("Could not find a valid BMP280 sensor, check wiring or "
                      "try a different address!"));
      Serial.print("SensorID was: 0x"); Serial.println(bmp.sensorID(),16);
      Serial.print("        ID of 0xFF probably means a bad address, a BMP 180 or BMP 085\n");
      Serial.print("   ID of 0x56-0x58 represents a BMP 280,\n");
      Serial.print("        ID of 0x60 represents a BME 280.\n");
      Serial.print("        ID of 0x61 represents a BME 680.\n");
      Serial.print("        ID of 0x76 represents a BME 680.\n");
      showError(); //ERROR
      neopixel.setPixelColor(0, neopixel.Color(100, 0, 0));
      neopixel.show();
      delay(3000);
    } else {
        Serial.println("BMP280 connected successfully");
        OLEDtestSuccess();
        neopixel.setPixelColor(0, neopixel.Color(0, 100, 0));
        neopixel.show();
        delay(500);
        
    }
    neopixel.clear();
    neopixel.show();
       
    /* Default settings from datasheet. */
    bmp.setSampling(Adafruit_BMP280::MODE_NORMAL,       /* Operating Mode. */
                    Adafruit_BMP280::SAMPLING_X2,       /* Temp. oversampling */
                    Adafruit_BMP280::SAMPLING_X16,      /* Pressure oversampling */
                    Adafruit_BMP280::FILTER_X16,        /* Filtering. */
                    Adafruit_BMP280::STANDBY_MS_500);   /* Standby time. */
    delay(100);
    
    Serial.println("BMP280: read once");

    Serial.print("Temperature: ");
    Serial.print(bmp.readTemperature());
    Serial.print(" ºC");

    Serial.print("\t Pressure = ");
    Serial.print(bmp.readPressure());
    Serial.print(" Pa");

    Serial.print("\t Approx altitude = ");
    Serial.print(bmp.readAltitude(SEA_LEVEL_PRESSURE)); /* Adjusted to local forecast! */
    Serial.print(" m");
    Serial.println();
    
    OLEDshowBMP280(bmp.readPressure()/100, bmp.readTemperature(), bmp.readAltitude(SEA_LEVEL_PRESSURE));
    delay(1000);

    Serial.println("==================  end test  ==================");
    Serial.println();
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

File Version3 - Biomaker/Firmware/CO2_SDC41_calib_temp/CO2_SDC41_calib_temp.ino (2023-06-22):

#include <Arduino.h>
#include <Wire.h>

//// Temperature sensor 
//#include <OneWire.h>
//#include <DallasTemperature.h>
//// Data wire is plugged into port 2 on the Arduino
//#define ONE_WIRE_BUS 2
// define DS18B20 data pin connection
#define DS18B20_PIN   A0

// OLED stuffs **********************
#include <Adafruit_GFX.h>
#include <Adafruit_SSD1306.h>
#define OLED_RESET -1
#define SCREEN_ADDRESS 0x3C
#define SCREEN_WIDTH 128 // OLED display width, in pixels
#define SCREEN_HEIGHT 64 // OLED display height, in pixels
uint32_t displayLimit = 1400;
uint32_t displayFactor = displayLimit / 48;
uint32_t meas_counter = 0;
int32_t thresholdPPM = 450;

Adafruit_SSD1306 display(SCREEN_WIDTH, SCREEN_HEIGHT, &Wire, OLED_RESET);

// """"""""""""""""""""""""""""""""""

// SCD4x **********************
const int16_t SCD_ADDRESS = 0x62;

unsigned long getDataTimer = 0;

const int cal_pin = 6;  // calibration button
unsigned long timeElapse = 0;//used to wait the sensor to stabilize before calibration

float co2, temperature, humidity;
  uint16_t calibration;
  uint8_t data[12], counter, repetition;
  uint8_t ret;
// """"""""""""""""""""""""""""""""""

// DS18B20 **********************
// Setup a oneWire instance to communicate with any OneWire devices (not just Maxim/Dallas temperature ICs)
//OneWire oneWire(ONE_WIRE_BUS);
//// Pass our oneWire reference to Dallas Temperature. 
//DallasTemperature sensors(&oneWire);




void setup() {
  
  Serial.begin(9600);
  // wait for serial connection from PC
  // comment the following line if you'd like the output
  // without waiting for the interface being ready
  while(!Serial);
  pinMode(cal_pin, INPUT_PULLUP); // entrada pulsado para calibrar, seteada como pulluppara poder conectar pulsador sin poenr resistencia adicional

  //Init OneWire
//   sensors.begin();


  // init I2C
  Wire.begin();

    delay(500);
    initDisplay();
    delay(100);

    showLogo_humus_text();
    delay(500);
    showLogo_oursci();
    delay(500);
    showLogo_hackteria();
    delay(500);
    showLogo_regosh();
    delay(5000);
    showLogo_biomaker();
    delay(5000);

  OLEDdrawBackground();

  // wait until sensors are ready, > 1000 ms according to datasheet
  delay(1000);
  
  // start scd measurement in periodic mode, will update every 5 s
  Wire.beginTransmission(SCD_ADDRESS);
  Wire.write(0x21);
  Wire.write(0xb1);
  Wire.endTransmission();
  // wait for first measurement to be finished
  delay(2000);
}
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
